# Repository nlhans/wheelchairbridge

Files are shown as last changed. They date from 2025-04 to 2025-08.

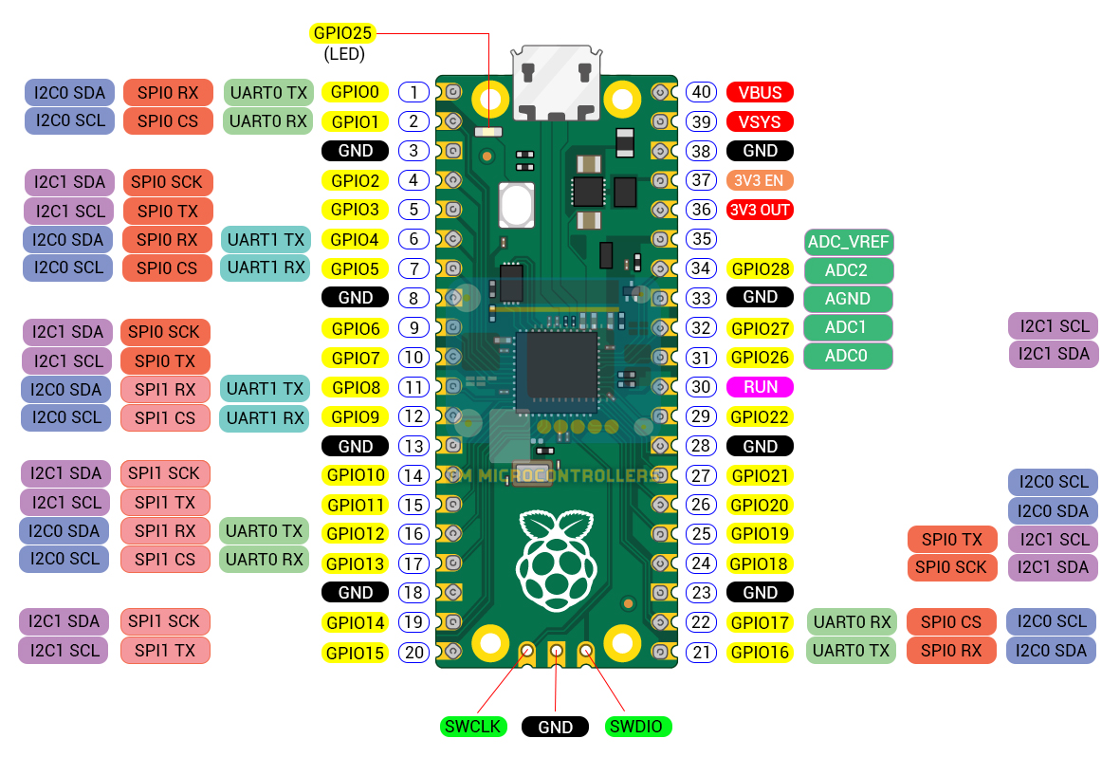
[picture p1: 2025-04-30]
datasheets/Raspberry-Pi-Pico-Pinout-2892229024.jpg

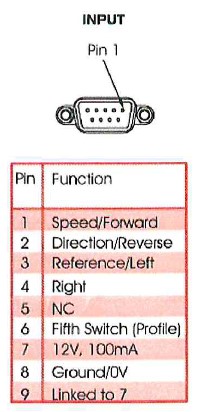
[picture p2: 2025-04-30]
datasheets/joystick.jpeg

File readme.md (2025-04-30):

#### wheelchair bridge 

Simple circuit using I2C digipot to emulate two-axis joystick following
(reasonable common) DB9 pinout.

Typically, a joystick for a wheelchair generates a +/- 1V around a 6V (mid 12V) center voltage. 

Note that the situation when the pico is powered off (and signals go to zero)

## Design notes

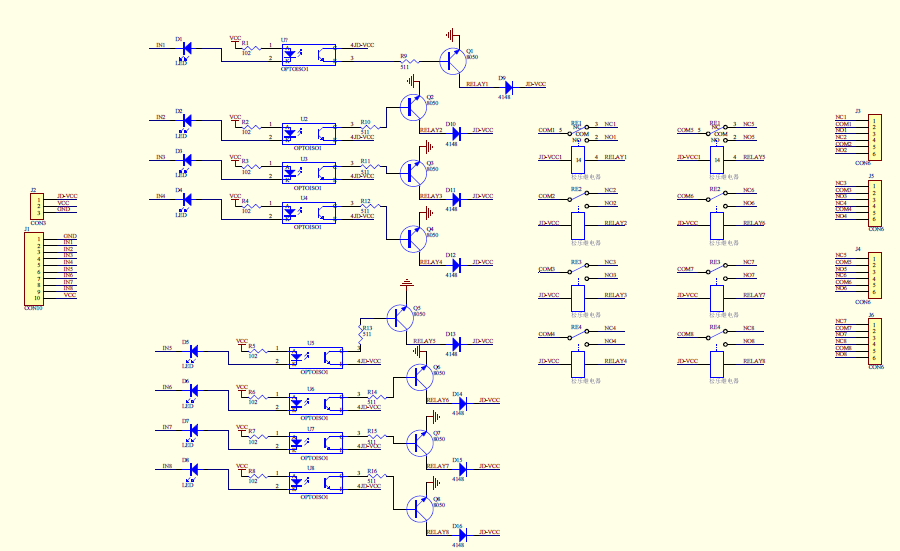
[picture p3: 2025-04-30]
datasheets/Elegoo+8+channel+relay+schematic-289185206.png

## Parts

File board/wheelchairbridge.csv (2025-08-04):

Id | Designator | Footprint | Quantity | Designation | Supplier and ref
1 | R10,R9 | R_0805_2012Metric | 2 | 0R
2 | RV1 | Potentiometer_Bourns_3314R-1_Vertical_Hole | 1 | 20k
3 | R14,R16,R15,R11,R3,R13,R5,R12,R1 | R_0805_2012Metric | 9 | 33k
4 | U6,U7,U5 | DIP-8_W7.62mm_Socket_LongPads | 3 | LH1512BB
5 | R24,R25,R23 | R_0805_2012Metric | 3 | R
6 | J2 | DSUB-9_Socket_Horizontal_P2.77x2.84mm_EdgePinOffset4.94mm_Housed_MountingHolesOffset4.94mm | 1 | female-to wheelchair
7 | J6 | NS-Tech_Grove_1x04_P2mm_Vertical | 1 | grove-Serial
8 | U2 | TSSOP-16_4.4x5mm_P0.65mm | 1 | AD5282
9 | U3,U4 | DIP-6_W7.62mm | 2 | TIL111
10 | R7,R8 | R_0805_2012Metric | 2 | 4k7
11 | C3,C1,C2,C6 | C_1206_3216Metric | 4 | 100nF
12 | D2 | LED_1206_3216Metric_Pad1.42x1.75mm_HandSolder | 1 | LED-yellow
13 | C5 | CP_Elec_D6.3mm_H6.1mm | 1 | 100uF
14 | J5 | TerminalBlock_bornier-2_P5.08mm | 1 | AlarmIn2
15 | J7,J9 | NS-Tech_Grove_1x04_P2mm_Vertical | 2 | grove-I2C
16 | J4 | TerminalBlock_bornier-2_P5.08mm | 1 | AlarmIn1
17 | J8,J10 | NS-Tech_Grove_1x04_P2mm_Vertical | 2 | grove-I2C-2
18 | M1 | RaspberryPi_PicoW_SocketTHT | 1 | Module_RaspberryPi_PicoW_SocketTHT
19 | R19,R26,R28,R27 | R_0805_2012Metric | 4 | 1k
20 | R2,R4,R6 | R_0805_2012Metric | 3 | 10k
21 | JP1 | PinHeader_1x02_P2.54mm_Vertical | 1 | power
22 | J3 | TerminalBlock_bornier-2_P5.08mm | 1 | 12V
23 | C4 | CP_Elec_D6.3mm_H6.1mm | 1 | 10uF
24 | D6,D5,D3 | LED_1206_3216Metric_Pad1.42x1.75mm_HandSolder | 3 | LED
25 | J1 | DSUB-9_Pins_Horizontal_P2.77x2.84mm_EdgePinOffset4.94mm_Housed_MountingHolesOffset4.94mm | 1 | male-joystick in
26 | U1 | TO-220-3_Vertical | 1 | LM7805_TO220
27 | R21,R17,R20,R22 | R_0805_2012Metric | 4 | 2k2

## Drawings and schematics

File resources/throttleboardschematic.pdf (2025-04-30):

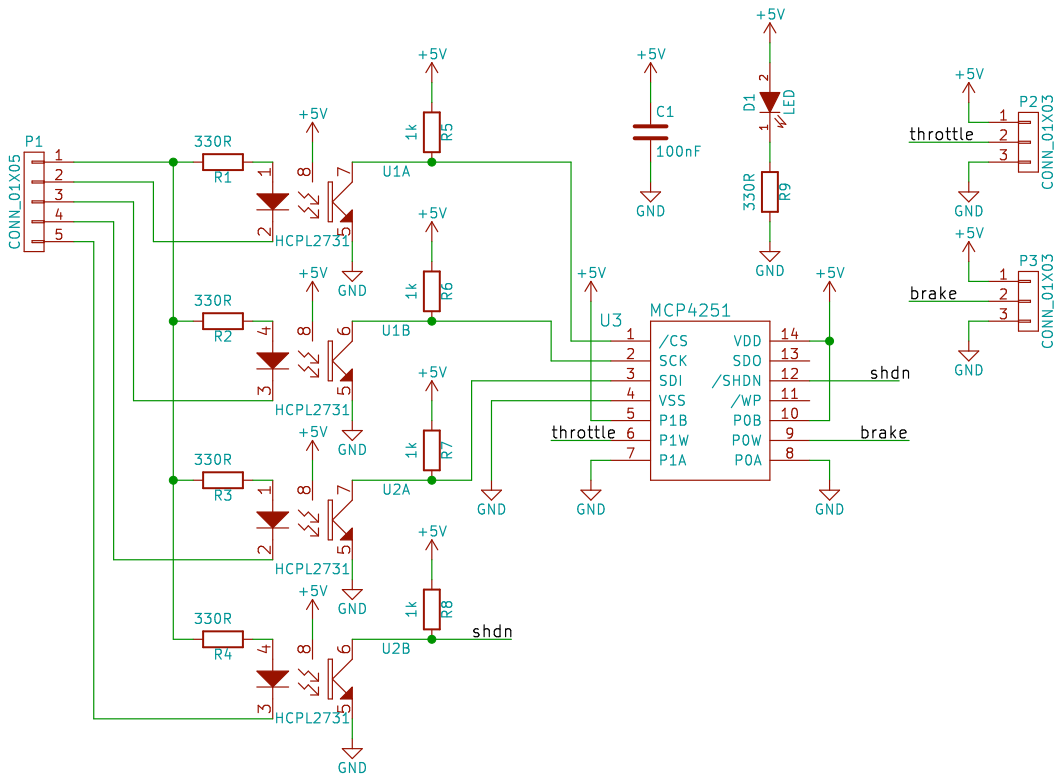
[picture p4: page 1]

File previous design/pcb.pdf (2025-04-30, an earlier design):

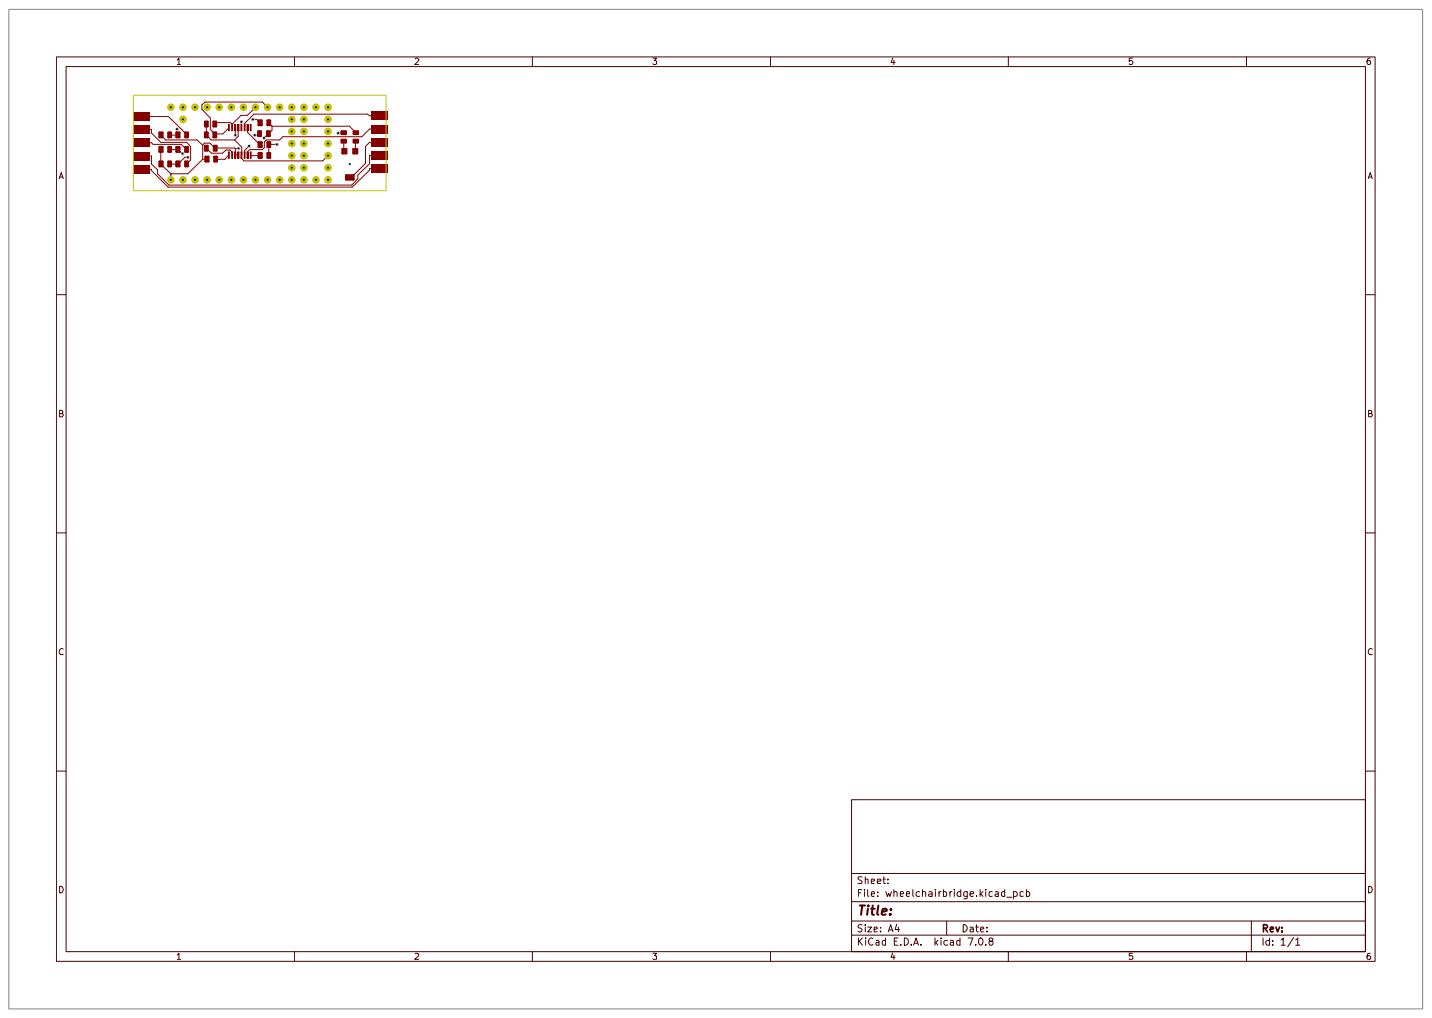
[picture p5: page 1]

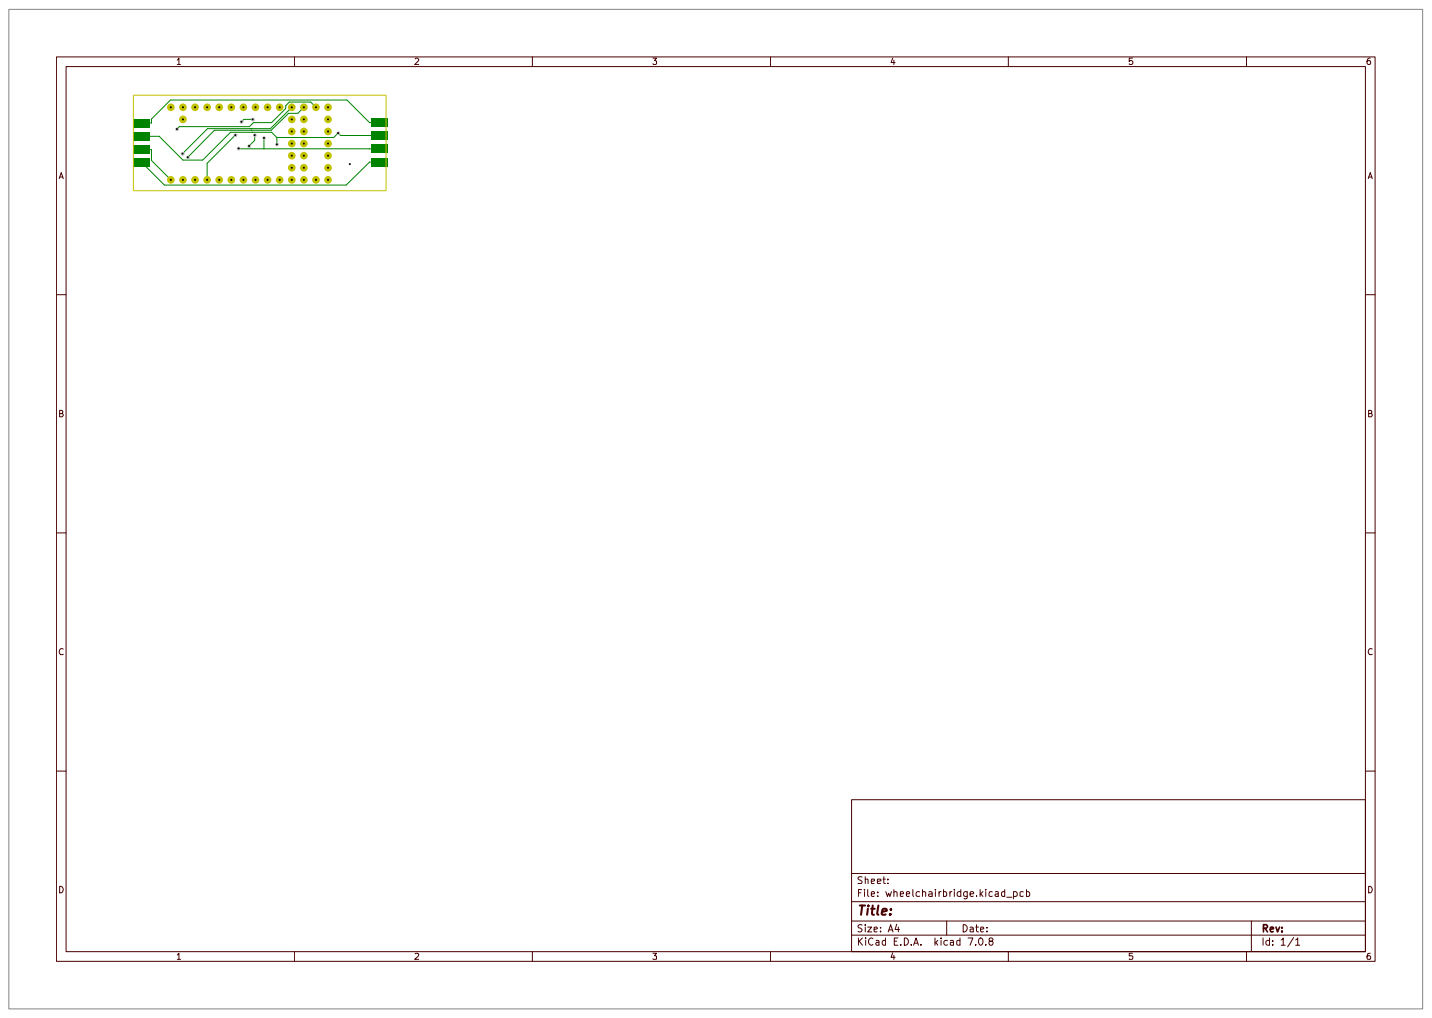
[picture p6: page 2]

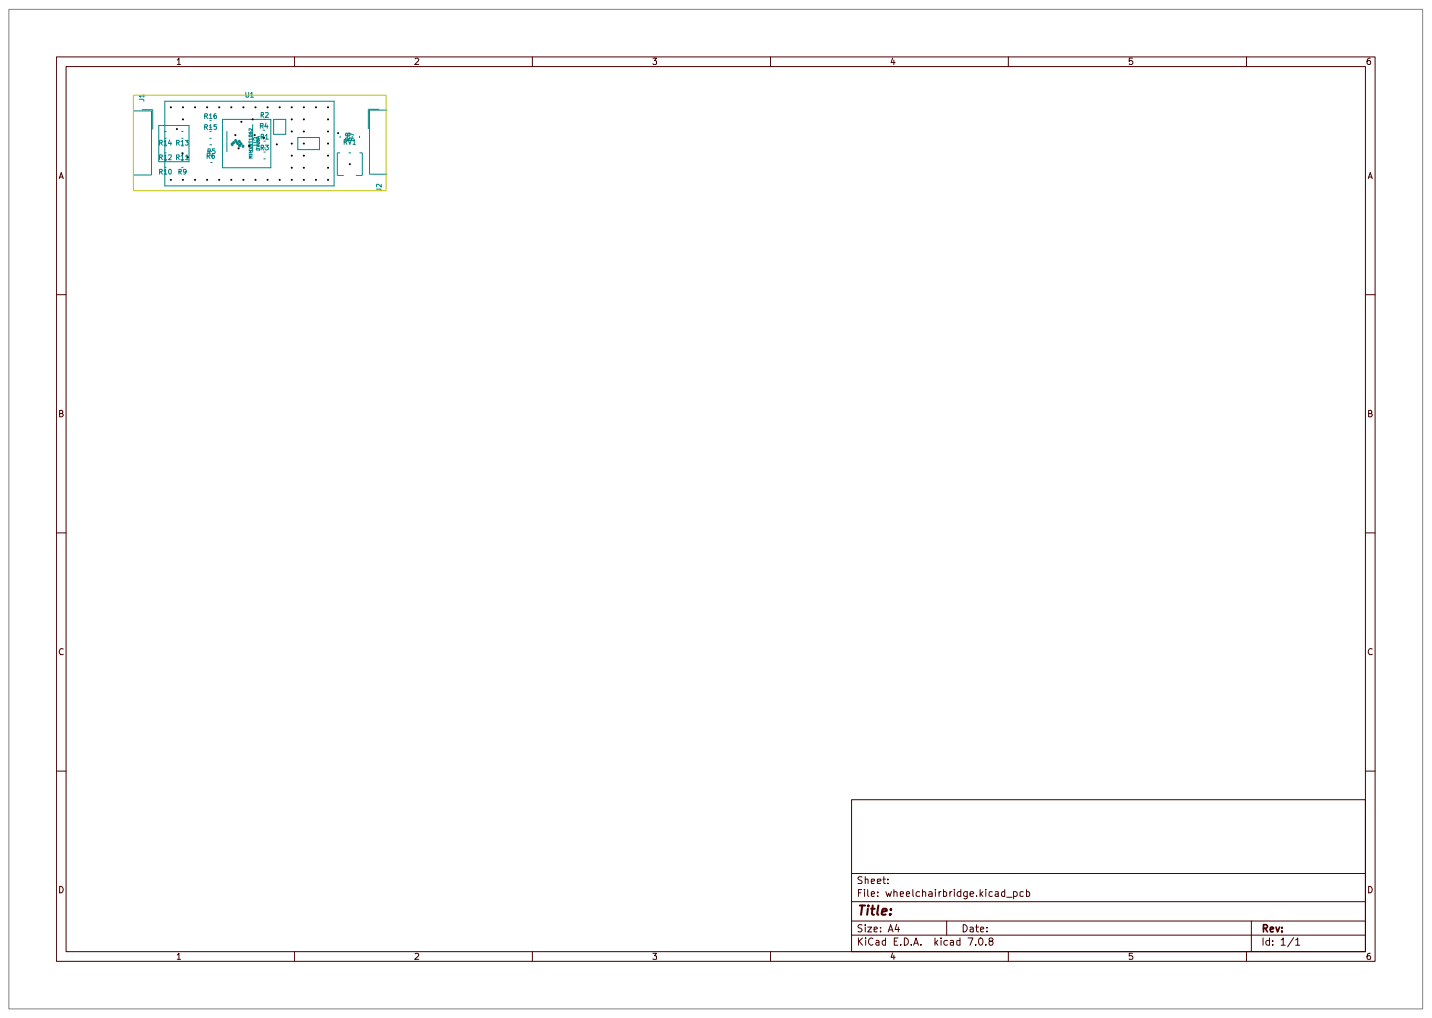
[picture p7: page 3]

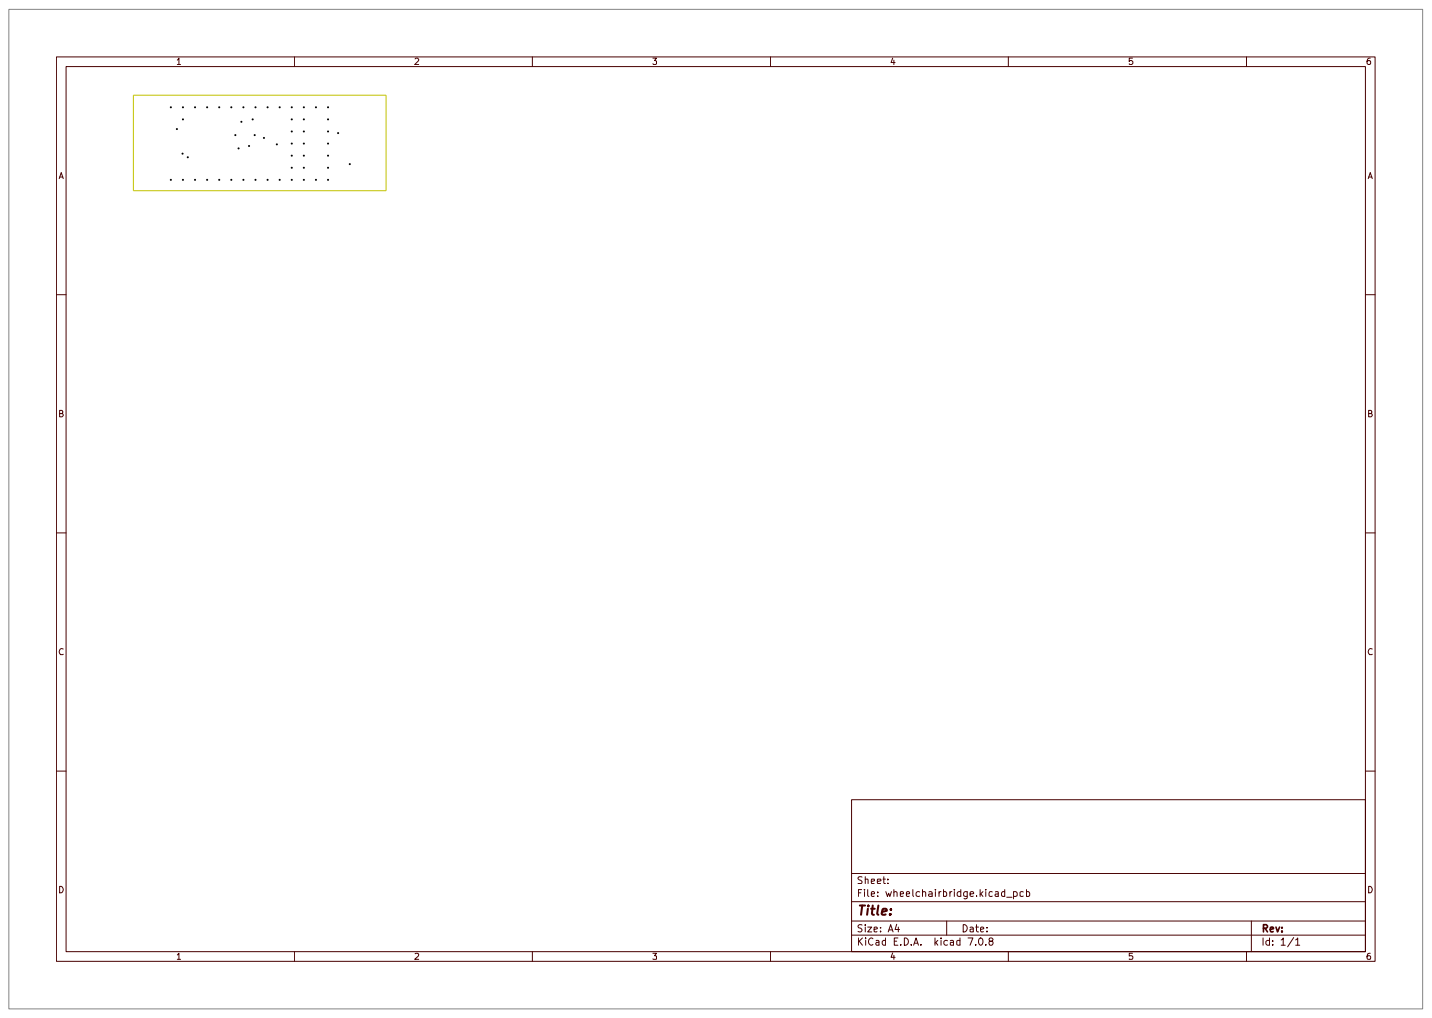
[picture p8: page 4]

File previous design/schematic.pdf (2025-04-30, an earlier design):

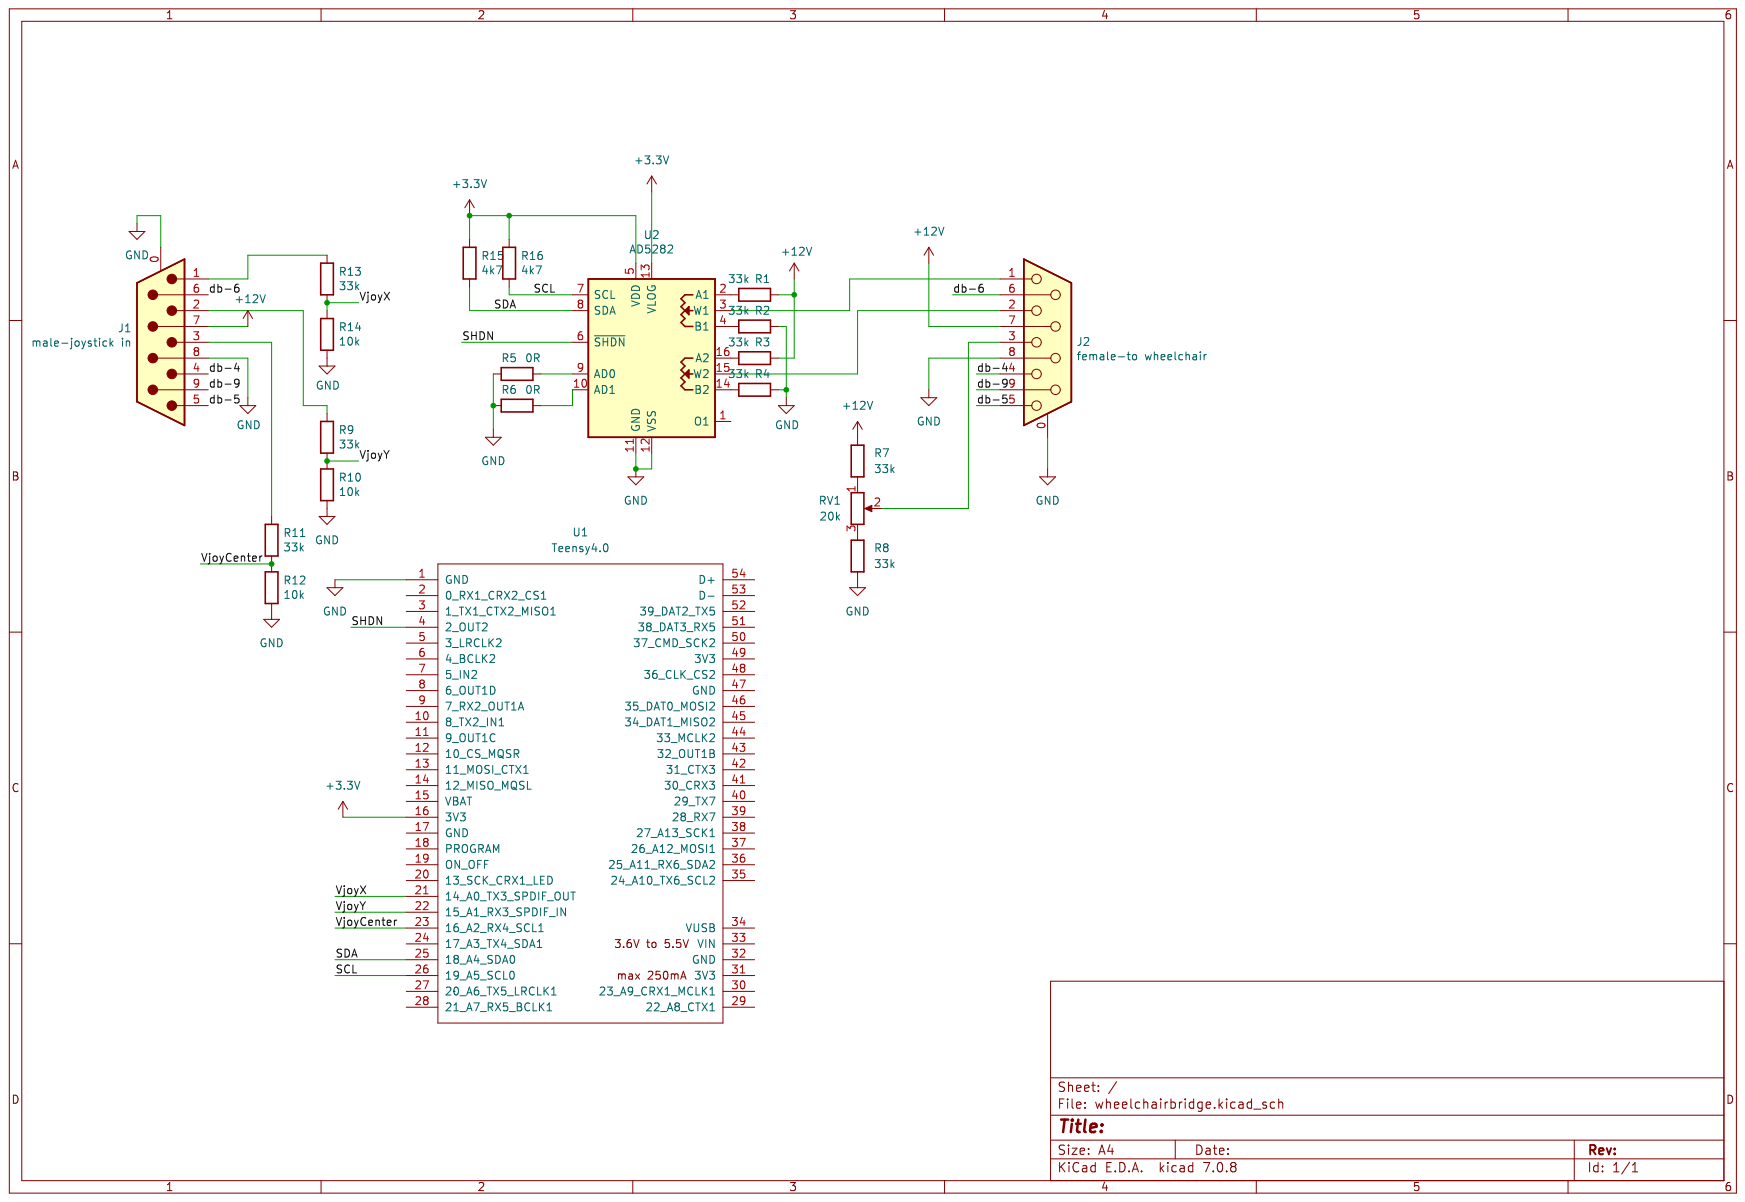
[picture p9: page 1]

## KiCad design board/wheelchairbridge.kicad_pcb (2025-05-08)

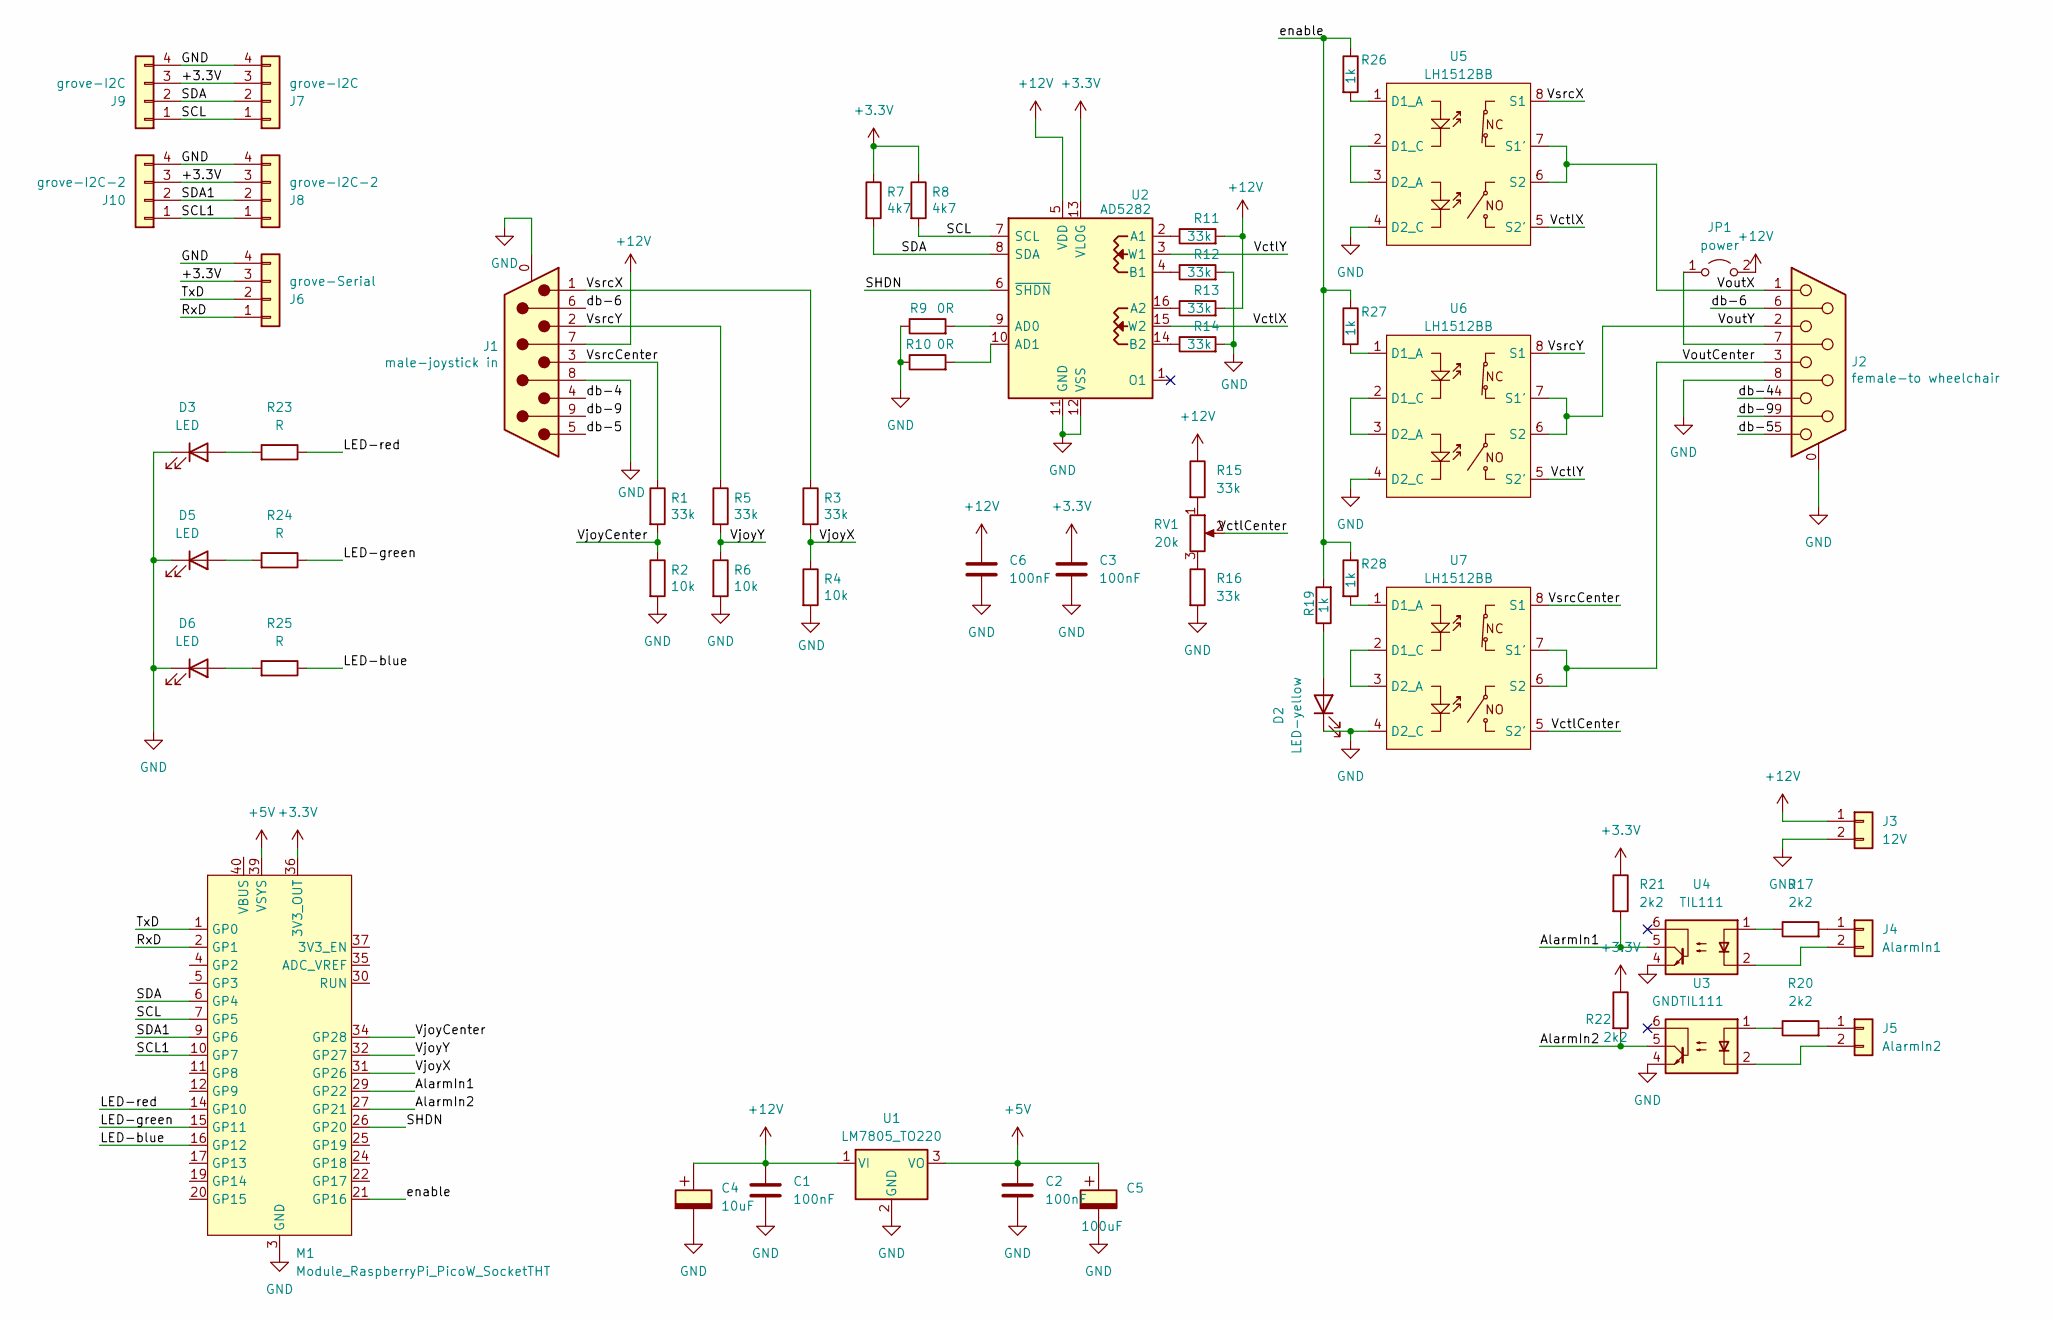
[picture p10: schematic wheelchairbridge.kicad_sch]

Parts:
C1, C2, C3, C6: 100nF; C_1206_3216Metric
C4: 10uF; CP_Elec_D6.3mm_H6.1mm
C5: 100uF; CP_Elec_D6.3mm_H6.1mm
D2: LED-yellow; LED_1206_3216Metric_Pad1.42x1.75mm_HandSolder
D3, D5, D6: LED; LED_1206_3216Metric_Pad1.42x1.75mm_HandSolder
J1: male-joystick in; DSUB-9_Pins_Horizontal_P2.77x2.84mm_EdgePinOffset4.94mm_Hou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
J2: female-to wheelchair; DSUB-9_Socket_Horizontal_P2.77x2.84mm_EdgePinOffset4.94mm_H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
J3: 12V; TerminalBlock_bornier-2_P5.08mm
J4: AlarmIn1; TerminalBlock_bornier-2_P5.08mm
J5: AlarmIn2; TerminalBlock_bornier-2_P5.08mm
J6: grove-Serial; NS-Tech_Grove_1x04_P2mm_Vertical
J7, J9: grove-I2C; NS-Tech_Grove_1x04_P2mm_Vertical
J8, J10: grove-I2C-2; NS-Tech_Grove_1x04_P2mm_Vertical
JP1: power; PinHeader_1x02_P2.54mm_Vertical
M1: Module_RaspberryPi_PicoW_SocketTHT; RaspberryPi_PicoW_SocketTHT
R1, R3, R5, R11, R12, R13, R14, R15, R16: 33k; R_0805_2012Metric
R2, R4, R6: 10k; R_0805_2012Metric
R7, R8: 4k7; R_0805_2012Metric
R9, R10: 0R; R_0805_2012Metric
R17, R20, R21, R22: 2k2; R_0805_2012Metric
R19, R26, R27, R28: 1k; R_0805_2012Metric
R23, R24, R25: R; R_0805_2012Metric
RV1: 20k; Potentiometer_Bourns_3314R-1_Vertical_Hole
U1: LM7805_TO220; TO-220-3_Vertical
U2: AD5282; TSSOP-16_4.4x5mm_P0.65mm
U3, U4: TIL111; DIP-6_W7.62mm
U5, U6, U7: LH1512BB; DIP-8_W7.62mm_Socket_LongPads

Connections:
+3.3V: C3.1, J6.3, J7.3, J8.3, J9.3, J10.3, M1.36 (3V3_OUT), R7.1, R8.1, R21.1, R22.1, U2.13 (VLOG)
+5V: C2.1, C5.1, M1.39 (VSYS), U1.3 (VO)
+12V: C1.1, C4.1, C6.1, J1.7, J3.1, JP1.2 (B), R11.2, R13.2, R15.1, U1.1 (VI), U2.5 (VDD)
/AlarmIn1: M1.29 (GP22), R21.2, U4.5
/AlarmIn2: M1.27 (GP21), R22.2, U3.5
/LED-blue: M1.16 (GP12), R25.1
/LED-green: M1.15 (GP11), R24.1
/LED-red: M1.14 (GP10), R23.1
/RxD: J6.1, M1.2 (GP1)
/SCL: J7.1, J9.1, M1.7 (GP5), R8.2, U2.7 (SCL)
/SCL1: J8.1, J10.1, M1.10 (GP7)
/SDA: J7.2, J9.2, M1.6 (GP4), R7.2, U2.8 (SDA)
/SDA1: J8.2, J10.2, M1.9 (GP6)
/SHDN: M1.26 (GP20), U2.6 (~SHDN)
/TxD: J6.2, M1.1 (GP0)
/VctlCenter: RV1.2, U7.5 (S2')
/VctlX: U2.15 (W2), U5.5 (S2')
/VctlY: U2.3 (W1), U6.5 (S2')
/VjoyCenter: M1.34 (GP28), R1.2, R2.1
/VjoyX: M1.31 (GP26), R3.2, R4.1
/VjoyY: M1.32 (GP27), R5.2, R6.1
/VoutCenter: J2.3, U7.6 (S2), U7.7 (S1')
/VoutX: J2.1, U5.6 (S2), U5.7 (S1')
/VoutY: J2.2, U6.6 (S2), U6.7 (S1')
/VsrcCenter: J1.3, R1.1, U7.8 (S1)
/VsrcX: J1.1, R3.1, U5.8 (S1)
/VsrcY: J1.2, R5.1, U6.8 (S1)
/db-4: J1.4, J2.4
/db-5: J1.5, J2.5
/db-6: J1.6, J2.6
/db-9: J1.9, J2.9
/enable: M1.21 (GP16), R19.2, R26.1, R27.1, R28.1
GND: C1.2, C2.2, C3.2, C4.2, C5.2, C6.2, D2.1 (K), D3.1 (K), D5.1 (K), D6.1 (K), J1.0 (PAD), J1.8, J2.0 (PAD), J2.8, J3.2, J6.4, J7.4, J8.4, J9.4, J10.4, M1.3 (GND), M1.8 (GND), M1.13 (GND), M1.18 (GND), M1.23 (GND), M1.28 (GND), M1.33 (GND), M1.38 (GND), R2.2, R4.2, R6.2, R9.1, R10.1, R12.2, R14.2, R16.2, U1.2 (GND), U2.11 (GND), U2.12 (VSS), U3.4, U4.4, U5.4 (D2_C), U6.4 (D2_C), U7.4 (D2_C)
unnamed: D2.2 (A), R19.1
unnamed: D3.2 (A), R23.2
unnamed: D5.2 (A), R24.2
unnamed: D6.2 (A), R25.2
unnamed: J4.1, R17.2
unnamed: J4.2, U4.2
unnamed: J5.1, R20.2
unnamed: J5.2, U3.2
unnamed: J2.7, JP1.1 (A)
unnamed: R15.2, RV1.1
unnamed: R16.1, RV1.3
unnamed: R17.1, U4.1
unnamed: R20.1, U3.1
unnamed: R11.1, U2.2 (A1)
unnamed: R13.1, U2.16 (A2)
unnamed: R9.2, U2.9 (AD0)
unnamed: R10.2, U2.10 (AD1)
unnamed: R12.1, U2.4 (B1)
unnamed: R14.1, U2.14 (B2)
unnamed: R26.2, U5.1 (D1_A)
unnamed: U5.2 (D1_C), U5.3 (D2_A)
unnamed: R27.2, U6.1 (D1_A)
unnamed: U6.2 (D1_C), U6.3 (D2_A)
unnamed: R28.2, U7.1 (D1_A)
unnamed: U7.2 (D1_C), U7.3 (D2_A)

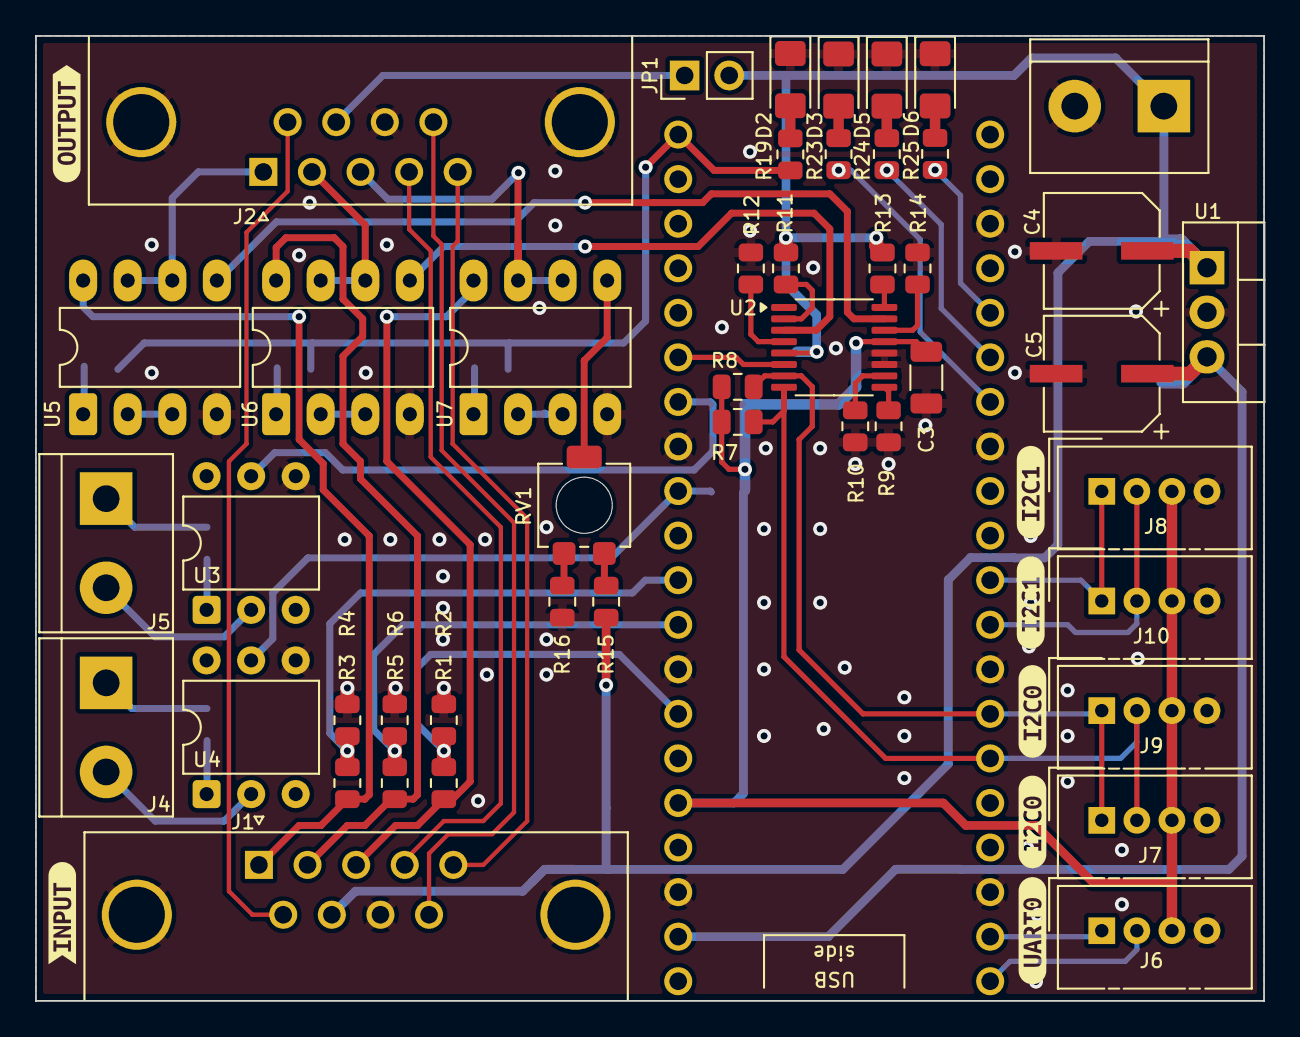
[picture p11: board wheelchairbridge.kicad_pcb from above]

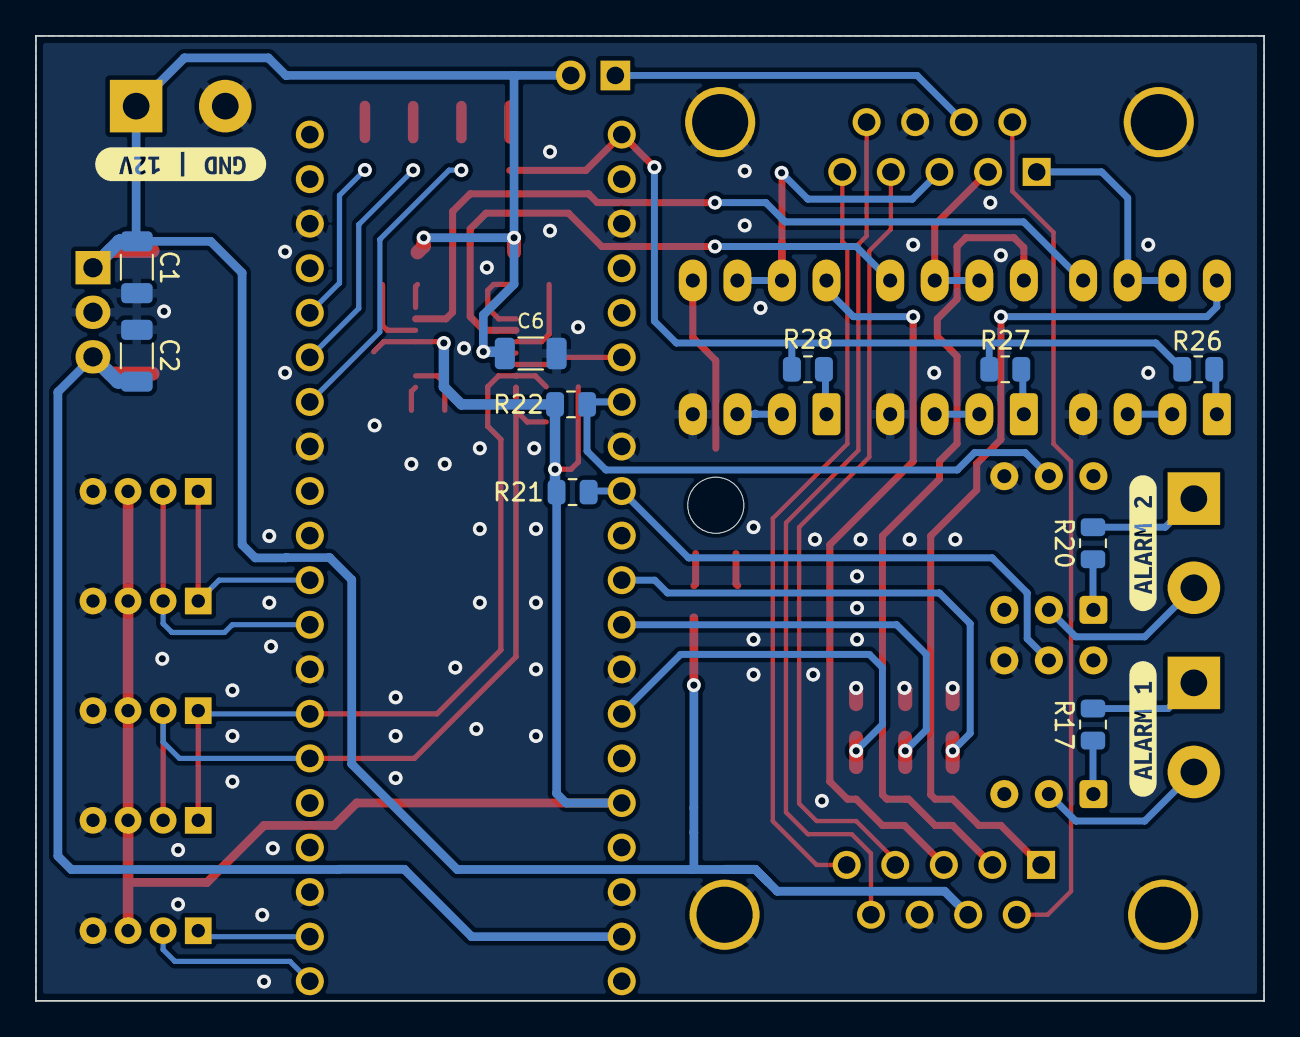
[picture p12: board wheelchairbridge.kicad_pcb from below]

Board: 2 copper layers, 70.0 x 55.0 mm, 67 parts (13 on the bottom side), 58 nets.

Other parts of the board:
kibuzzard-681B4A1A, kibuzzard-681B4A1A#2: G***; kibuzzard-681B4A1A
kibuzzard-681B4A2D, kibuzzard-681B4A2D#2: G***; kibuzzard-681B4A2D
kibuzzard-681B4A44: G***; kibuzzard-681B4A44
kibuzzard-681B47BC: G***; kibuzzard-681B47BC
kibuzzard-681B47CA: G***; kibuzzard-681B47CA
kibuzzard-681B4932: G***; kibuzzard-681B4932
kibuzzard-681C614D: G***; kibuzzard-681C614D
kibuzzard-681C6150: G***; kibuzzard-681C6150

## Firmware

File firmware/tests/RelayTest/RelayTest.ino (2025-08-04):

#include "AD524X.h"

#define LED_D3 10
#define LED_D5 11
#define LED_D6 12
#define INTERCEPT 16
#define RDAC_SHDN 20

#define AXIS_X_IN 26 // ADC0
#define AXIS_Y_IN 27 // ADC1
#define AXIS_C_IN 28 // ADC2
#define AXIS_X_OUT 1
#define AXIS_Y_OUT 0

// 3.3V = voltage reference
// 1.007f = +0.7% (measurements were reading too low)
// (10+33)/10 = resistive division ratio
#define AXIS_IN_LSB_TO_V (3.3f * 1.007f/4095.0f * (10.0f + 33.0f) / (10.0f))

AD524X AD01(0b0101100);

void setup()
{
  delay(1000);
  analogReadResolution(12);

  pinMode(LED_D3, OUTPUT); // LED D3
  pinMode(LED_D5, OUTPUT); // LED D5
  pinMode(LED_D6, OUTPUT); // LED D6
  pinMode(INTERCEPT, OUTPUT);

  pinMode(RDAC_SHDN, OUTPUT);
  digitalWrite(RDAC_SHDN, HIGH);

  Serial.begin(115200);
  Serial.println();
  Serial.println(__FILE__);
  Serial.print("AD524X_LIB_VERSION: ");
  Serial.println(AD524X_LIB_VERSION);

  Wire.begin();
  Wire.setSDA(4);
  Wire.setSCL(5);
  Wire.setClock(400000);

  bool b = AD01.begin();
  Serial.println(b ? "true" : "false");
  Serial.println(AD01.isConnected());
}

int ticks = 0;

void loop()
{
  uint16_t inX = analogRead(AXIS_X_IN);
  uint16_t inY = analogRead(AXIS_Y_IN);
  uint16_t inC = analogRead(AXIS_C_IN);

  ticks ++;
  if (ticks == 2) {
    digitalWrite(INTERCEPT, HIGH);
  } else if (ticks >= 4) {
    digitalWrite(INTERCEPT, LOW);
    ticks = 0;
  }

  float actualVM = inC * AXIS_IN_LSB_TO_V * 2;
  float desiredXout = inX * AXIS_IN_LSB_TO_V / (actualVM / 12.0f);
  float desiredYout = inY * AXIS_IN_LSB_TO_V / (actualVM / 12.0f);

  // https://www.wolframalpha.com/input?i=%2833+%2B+20*x+%2F255%29+%2F++%2833+%2B+20+%2B+33%29+*12+%3D+y%2C+solve+for+x
  // (copy and paste into browser, Arduino IDE doesn't open this link properly)
  // +16 = calibration value
  int outX = constrain(17/8.0* (43 * desiredXout - 198) + 16, 0, 255);
  int outY = constrain(17/8.0* (43 * desiredYout - 198) + 16, 0, 255);
  
  AD01.write(AXIS_X_OUT, outX);
  AD01.write(AXIS_Y_OUT, outY);


  Serial.print("[In] X: ");
  Serial.print(inX * AXIS_IN_LSB_TO_V);x
  Serial.print("V ");
  Serial.print(inX);

  Serial.print(", Y: ");
  Serial.print(inY * AXIS_IN_LSB_TO_V);
  Serial.print("V ");
  Serial.print(inY);

  Serial.print(", C: ");
  Serial.print(inC * AXIS_IN_LSB_TO_V);
  Serial.print("V ");
  Serial.print(inC);

  Serial.print(" [Out] X: ");
  Serial.print(desiredXout);
  Serial.print("V ");
  Serial.print(outX);

  Serial.print(", Y: ");
  Serial.print(desiredYout);
  Serial.print("V ");
  Serial.print(outY);

  Serial.println();
  delay(50);

  // digitalWrite(INTERCEPT, HIGH);
  //   AD01.write(0, 128);
  //   AD01.write(1, 128);
  //   delay(5000);
    
  // digitalWrite(INTERCEPT, LOW);
  // for (int val = 0; val < 255; val+=16)
  // {
  //   AD01.write(0, val);
  //   AD01.write(1, val);
  //   Serial.println(val);
  //   delay(1000);
  // }
}

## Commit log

2025-04-30 added readme
    [wheelchairbridge.kicad_pcb, wheelchairbridge.kicad_sch]
2025-05-07 Added Solid State relays for low-power signal switching. Switch from edge to regular DB9 connectors Refactored schematic PCB layout
    [wheelchairbridge.kicad_pcb, wheelchairbridge.kicad_sch]
2025-05-08 Alarm labels were wrong Added 100nF cap on 12V for digipot
    [wheelchairbridge.kicad_pcb, wheelchairbridge.kicad_sch]
2025-08-04 Interactive BOM for assembly Test Arduino Sketch with R-DAC and relays.
    [wheelchairbridge.csv]
